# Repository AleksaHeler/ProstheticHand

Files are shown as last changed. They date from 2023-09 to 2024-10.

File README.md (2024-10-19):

# OpenHand
 
Our attempt at a prosthetic hand controlled by muscle EMG sensors, using linear actuators to move mechanically linked fingers. Implementing our own 3D models (ME), schematic & PCB design of main control board (EE) and software solution (SW).

## Proof of concept

Our (actually second) proof of concept, is using our own PCBs with STM32, our own mechanical design, and some basic software running on STM32 reacting on button press or EMG sensor activation.

For now, this approach seems promising, and only thing left to be changed is the motors used. We use linear actuators, which seem to be exactly what we need, but for now they don't have any position feedback. To solve that we will be using motors with built-in encoders in future, and monitoring their position with STM32 HW timer functions for encoders. Preliminary testing for that worked perfectly, we could always know the position of the motor based on the encoder value, and using endstops we can also calibrate the travel, and using current limiting H bridge motor drivers, we can control the force applied. 

Here are some screenshots of the current status:

### Finger design. Completely mechanical linkage, with linear actuator
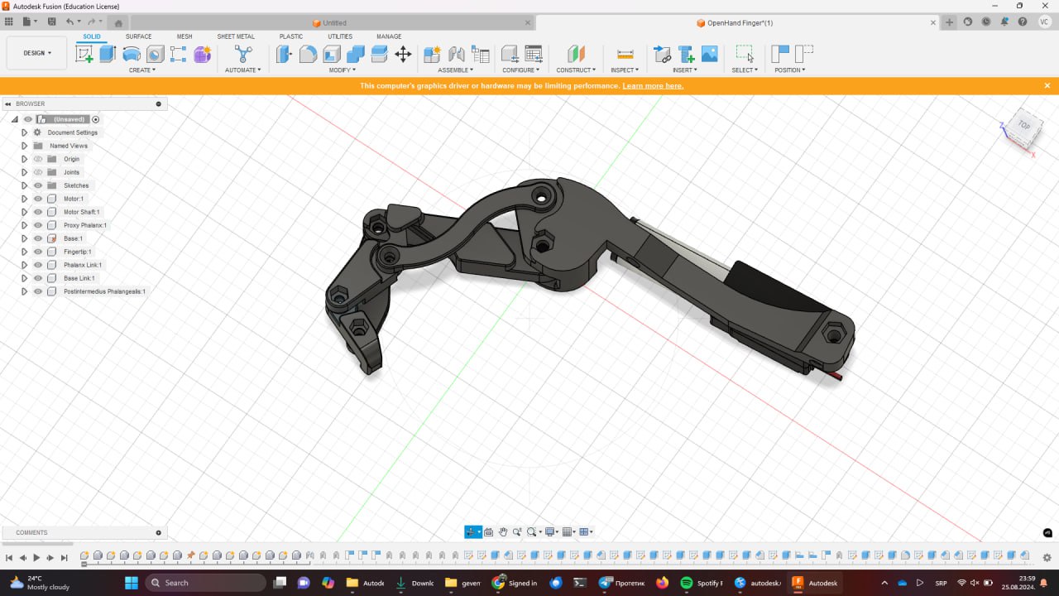
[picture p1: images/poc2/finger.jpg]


### Our custom PCB, with many components including EMG sensors, H bridge motor drivers, etc.
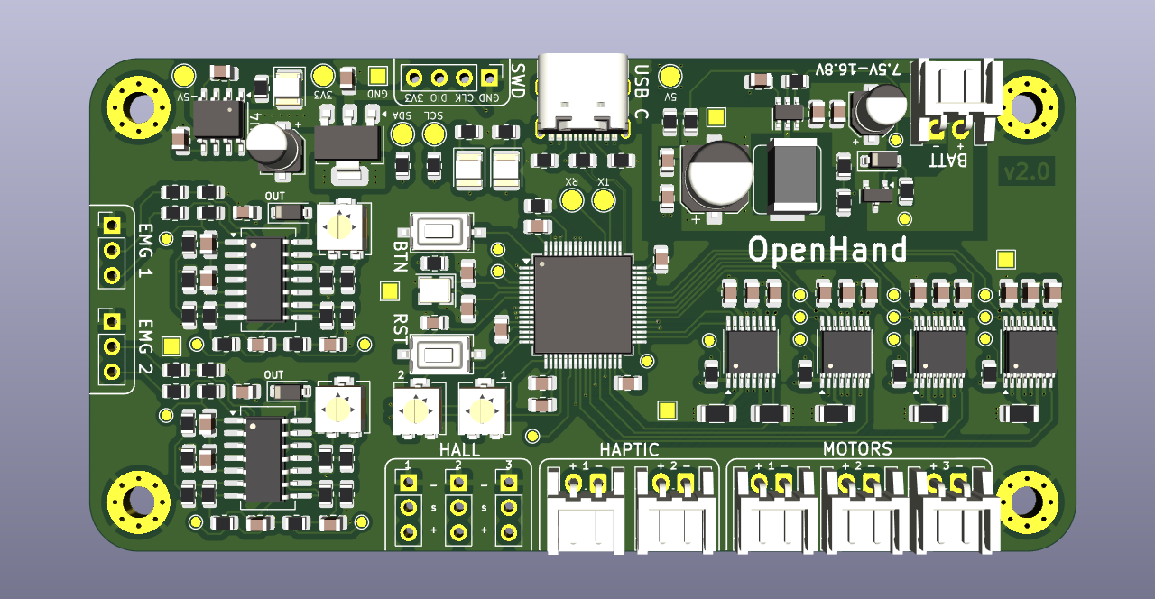
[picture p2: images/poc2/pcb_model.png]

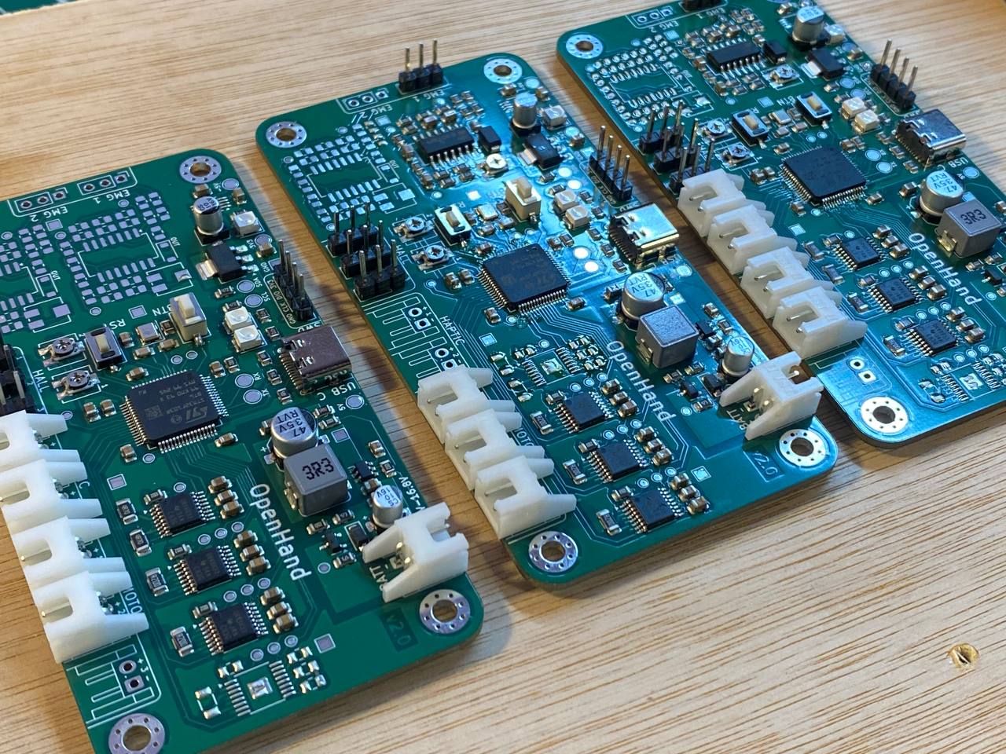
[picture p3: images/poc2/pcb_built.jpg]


### Also some EMG sensor readings (before additional filtering)
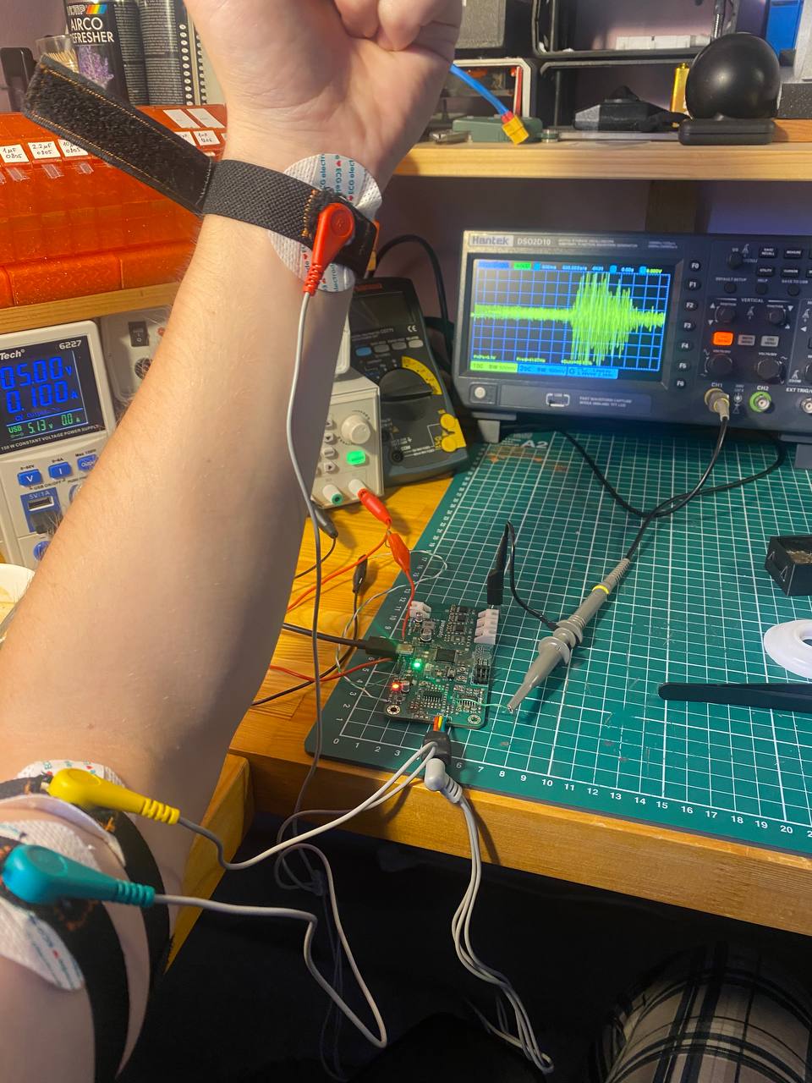
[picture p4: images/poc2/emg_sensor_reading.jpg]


### Now, the whole prototype of the hand (3D printed, batteries, PCB, 3x fingers with motors)
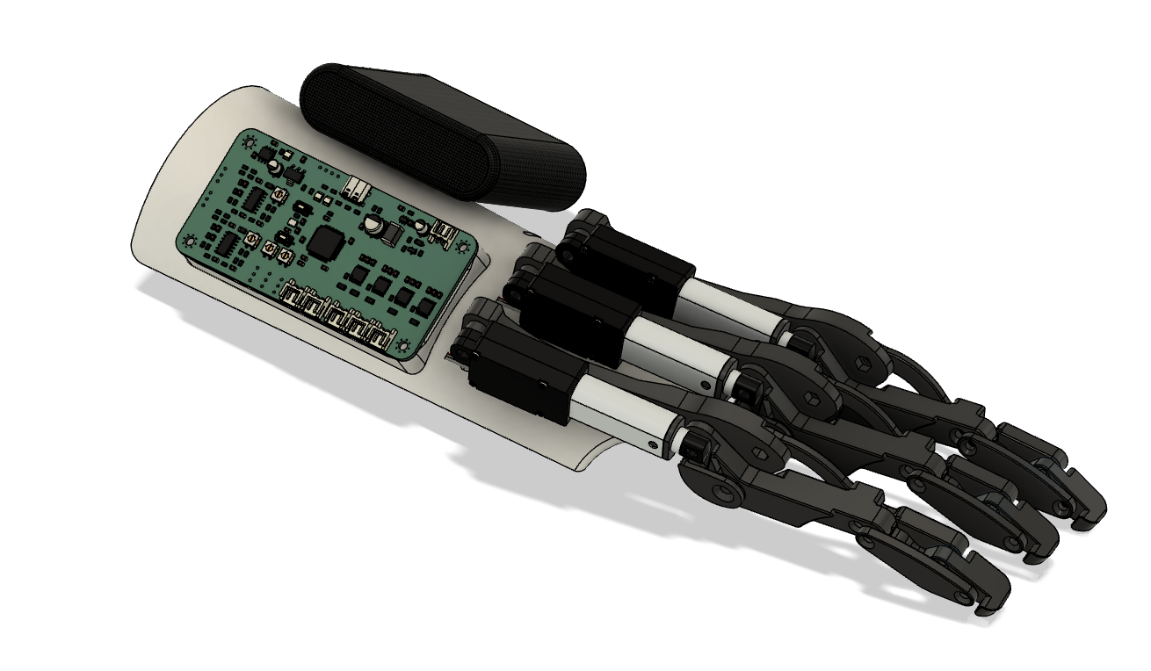
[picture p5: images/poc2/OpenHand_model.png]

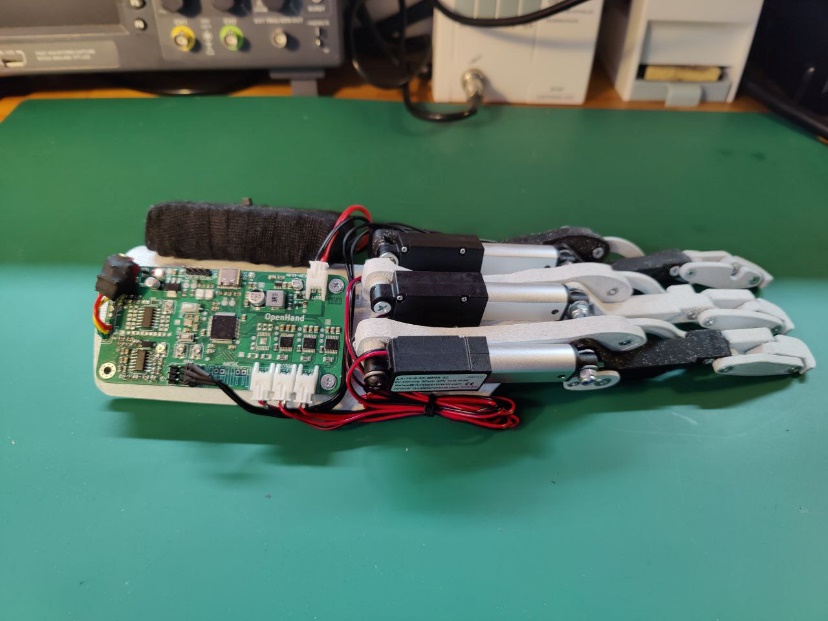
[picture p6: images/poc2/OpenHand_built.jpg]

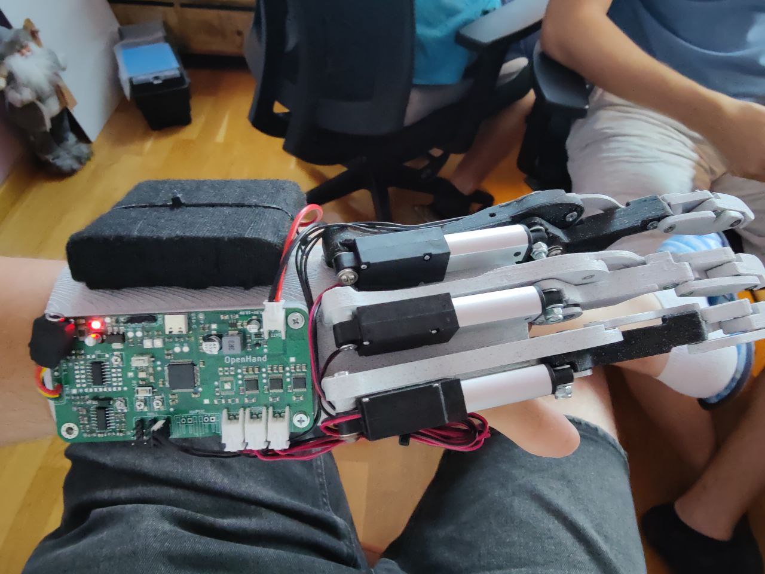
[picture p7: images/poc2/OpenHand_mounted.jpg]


## Example videos of OpenHand in action

Here are some videos of the project for now. Nice to see it finally come together, although this is still early in development, and some things will be changed, and a lot of things will be made to look even prettier.

Note: you might have to download .mp4 videos if GitHub doesn't support playback in browser.

### Showing the response when EMG reading muscle activity 
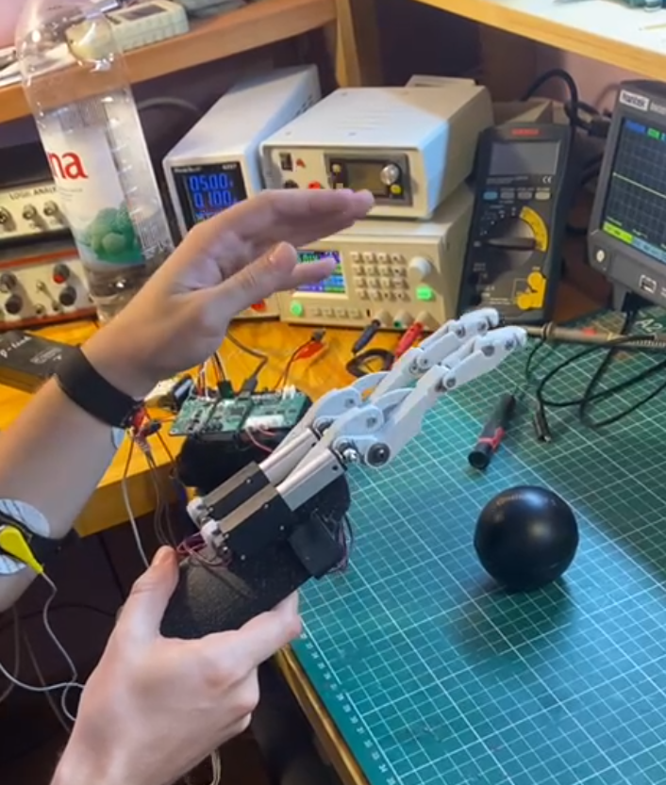
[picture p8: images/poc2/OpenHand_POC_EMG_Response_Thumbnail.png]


### Simple demonstration of holding a bottle
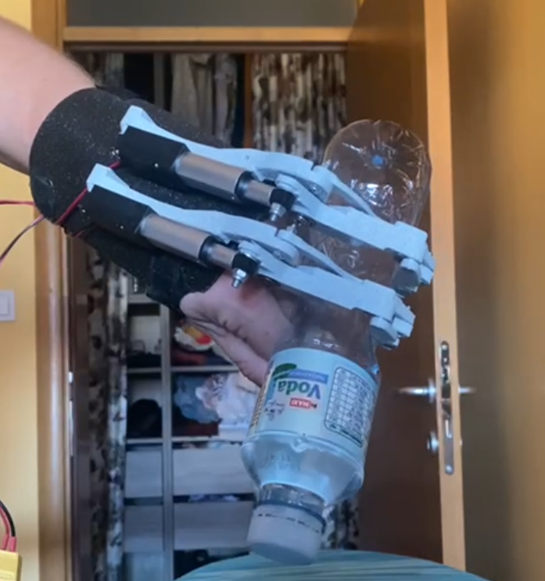
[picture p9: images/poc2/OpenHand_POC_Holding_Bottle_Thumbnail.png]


### Demo: holding a can of soda
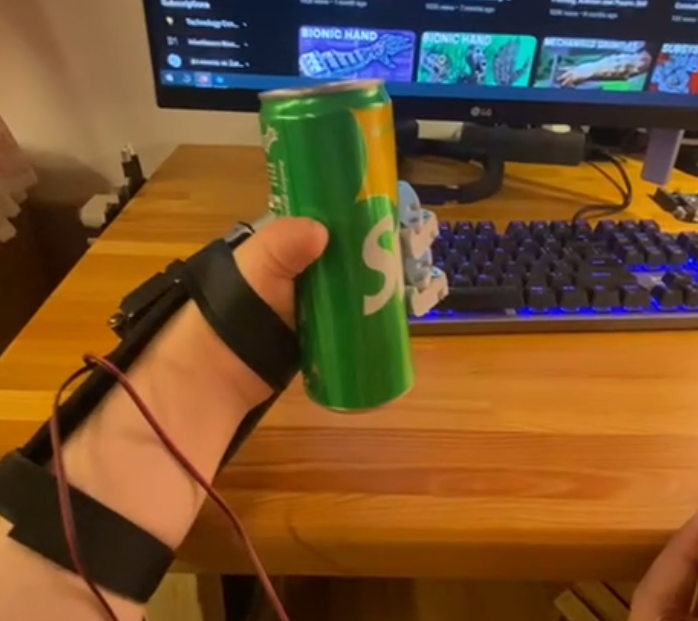
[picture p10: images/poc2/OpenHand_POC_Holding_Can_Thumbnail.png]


### Demo: holding a multimeter
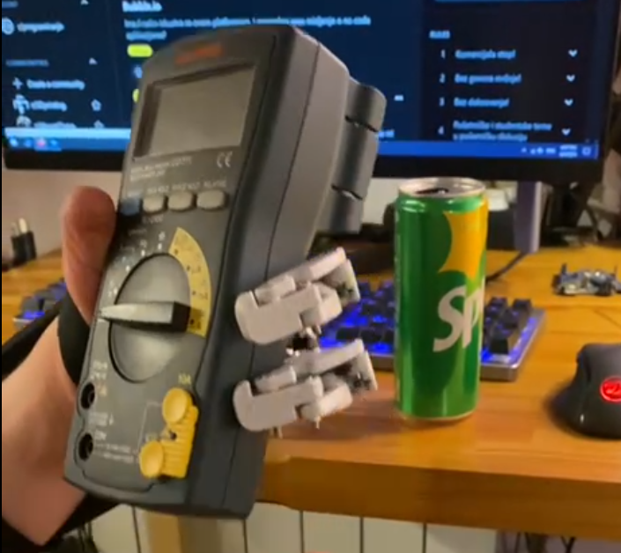
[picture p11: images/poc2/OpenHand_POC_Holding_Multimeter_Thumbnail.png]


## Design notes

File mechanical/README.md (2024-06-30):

# Mechanical designs for the prosthetic hand project

## Initial design based on plaster mold of the hand

In folder **OpenHand** you can find the [Fusion360 file of the prosthetic hand](OpenHand/OpenHand.f3d), described below (as well as a .STEP file).

Here is the (somewhat modified and cleaned up) scan of the plaster/clay mold we made of the base, by pressing it over the arm:
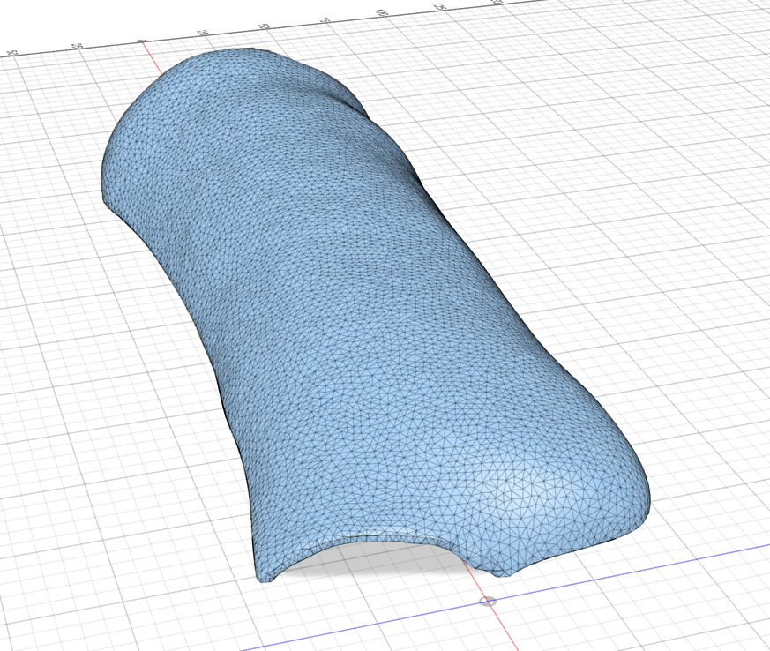
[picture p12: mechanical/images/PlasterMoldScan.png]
Plaster mold


After it is imported into Fusion 360, we can create a more basic shape following its dimensions and profile somewhat, so we will make a parametric design to be later 3D printed:
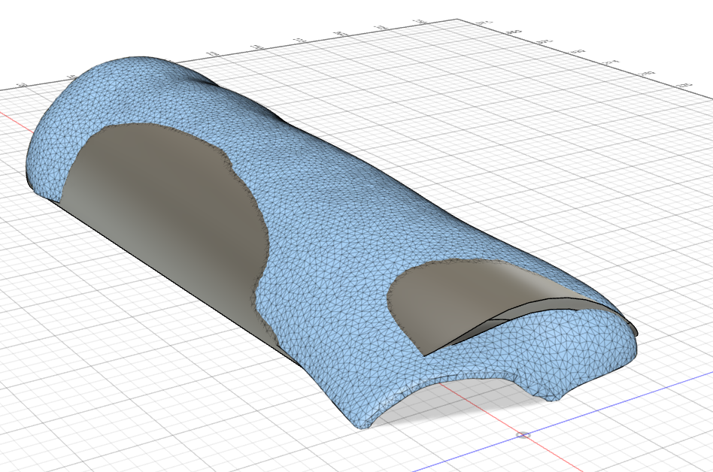
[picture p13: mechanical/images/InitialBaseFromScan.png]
Initial base model


After adding finger design by [fflori4n](https://github.com/fflori4n), motor, PCB and battery 3D models:
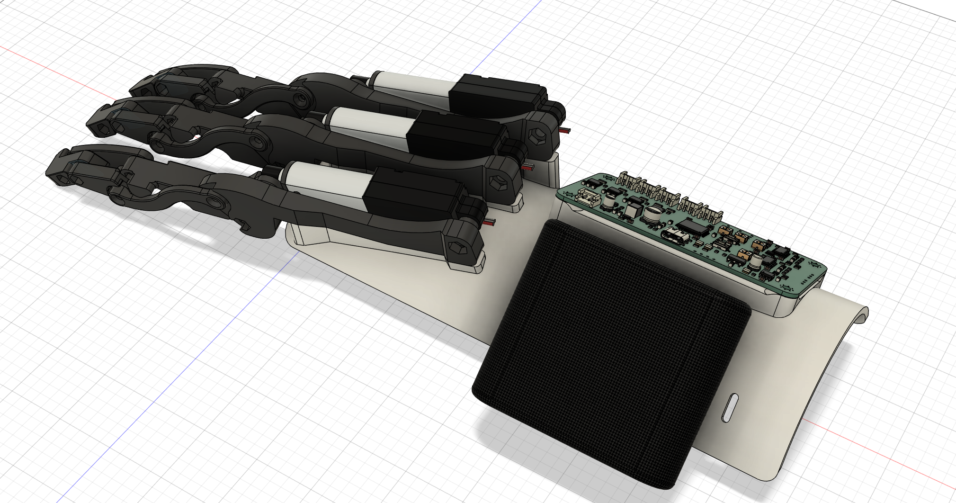
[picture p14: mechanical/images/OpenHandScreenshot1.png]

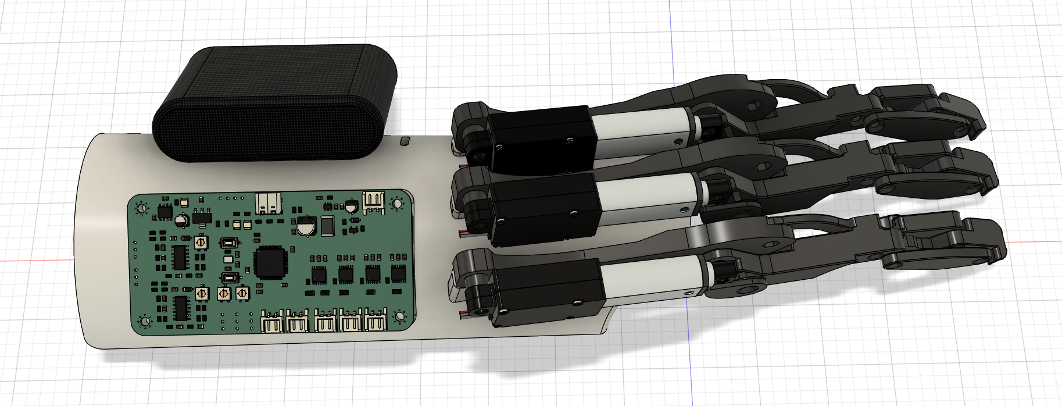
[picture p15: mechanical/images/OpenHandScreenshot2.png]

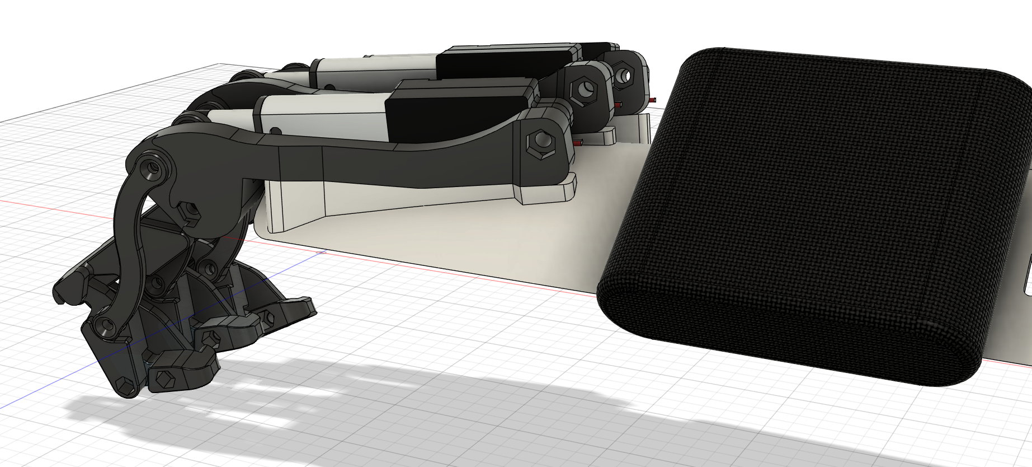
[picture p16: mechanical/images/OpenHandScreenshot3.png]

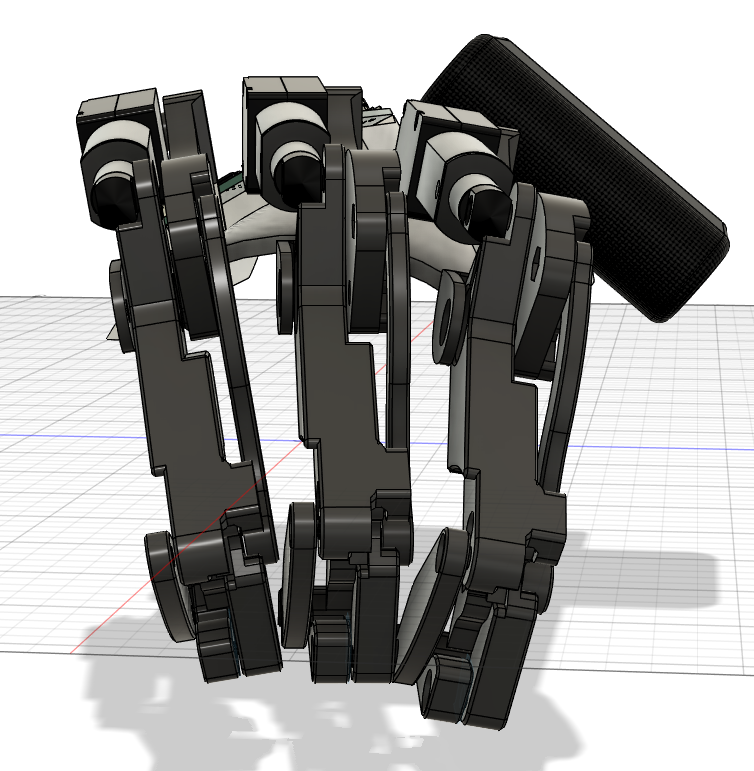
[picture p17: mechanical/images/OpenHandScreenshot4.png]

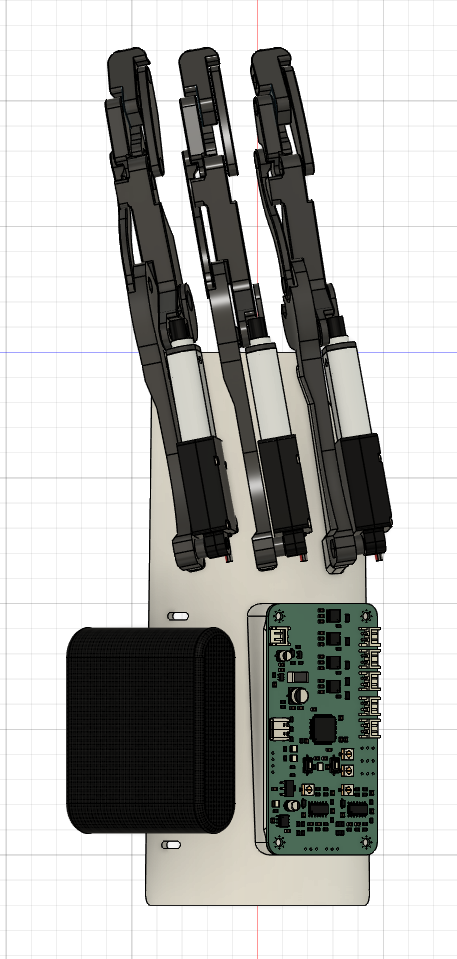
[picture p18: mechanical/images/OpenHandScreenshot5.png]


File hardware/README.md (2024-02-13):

# Hardware & PCB designs of the prosthetic hand project

For designing those we use [KiCAD](https://www.kicad.org/download/). Good tutorial can be found [here](https://www.youtube.com/playlist?list=PL3bNyZYHcRSUhUXUt51W6nKvxx2ORvUQB). Although it's for a bit older version of the KiCAD it is still usefull.

For now we have two designs: DevBoard and OpenHand. First one is for proof of concept, while other one is still in development and meant to be used as initial version to build upon.

## DevBoard

Firstly we haver here a development board, custom made for our purpose of having EMG sensors and servo motors connected. Also a couple of buttons/pots etc. for easier debugging/testing. Schematic can be found [here](DevBoard/schematic.pdf).

We will be using [ESP32 S3](https://api.riot-os.org/group__cpu__esp32__esp32s3.html). So in this desin, we're using the ESP32 S3 devboard, but later on we will just use the ESP32 microprocessor.

The boards will be ordered from an online PCB manufacturer, in our case JLC PCB.

DevBoard features:
 - battery/power supply connector
 - 3x servo connectors (with current sensing over 0.1 ohm shunts, and filter for current sensing signal as it is a bit noisy)
 - 2x EMG sensor connectors (signal goes trough RC low-pass filter on its way to the uC)
 - 4x dip switches for easy configuration (easily change code logic on-the go, without re-flashing the board)
 - 2x push buttons (with on-board pullups and HW debounce filter)
 - 2x trim pots and one 'normal' potentiometer (with RC low-pass filter to get rid of some noise from cheap pots)
 - 2x debug LEDs (red/green)
 - 5V regulator for the ESP32 DevBoard
 - input/battery voltage sensing
 - reverse protection diode (would be nice to upgrade to a 'smarter' variant with MOSFET later)
 - 2 layer PCB, components on one side, mix of SMD/THT components
 - a lot of test point pads on the board for all the signals

For now, this DevBoard should give us enough functionality to make some version of a working prototype, but the wishlist for the actual PCB will be updated as we come across new stuff.

### Devboard pictures

#### Schematic

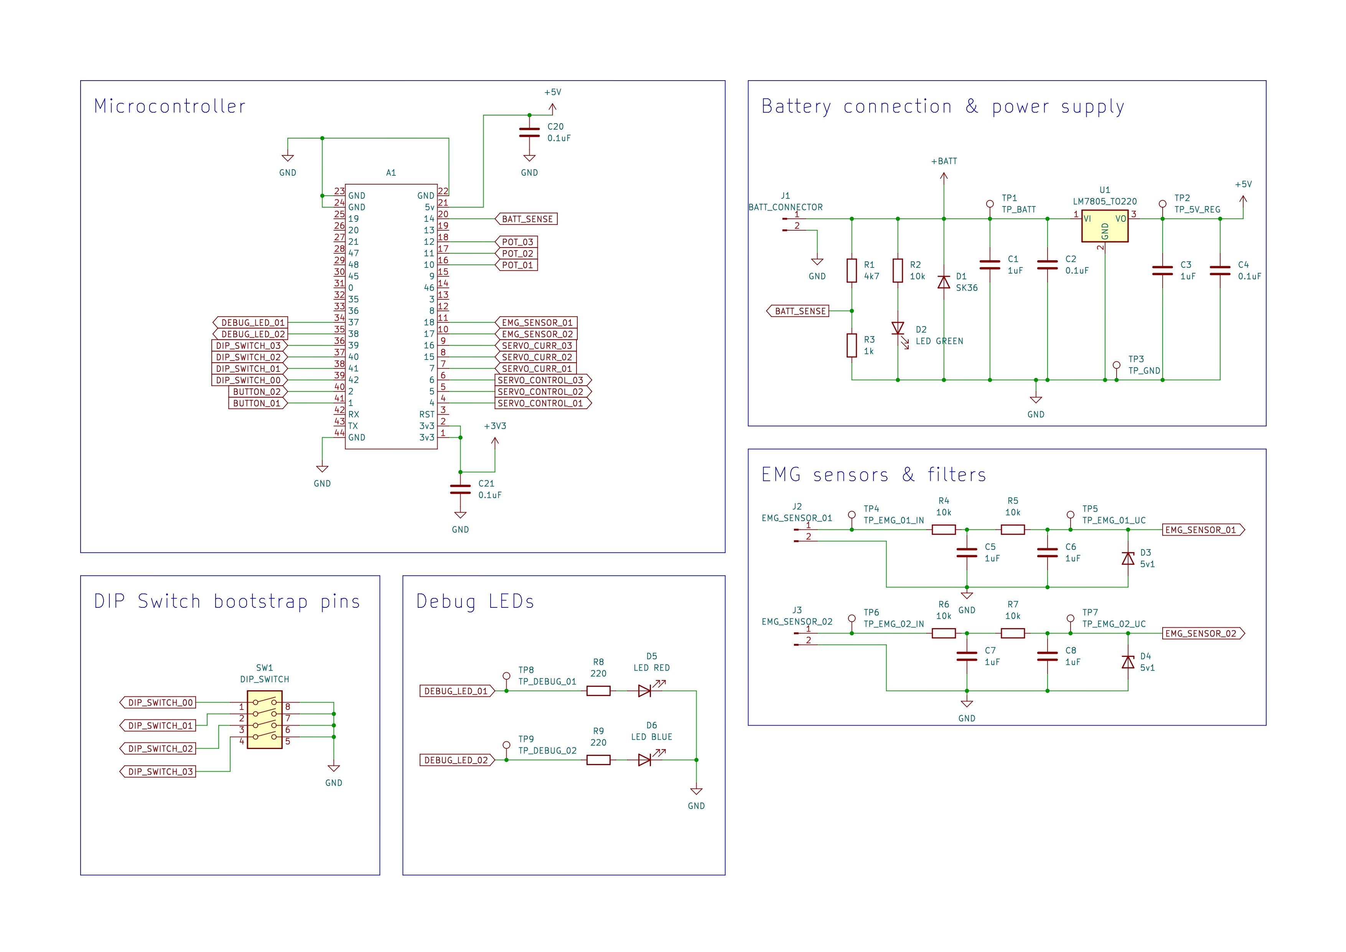
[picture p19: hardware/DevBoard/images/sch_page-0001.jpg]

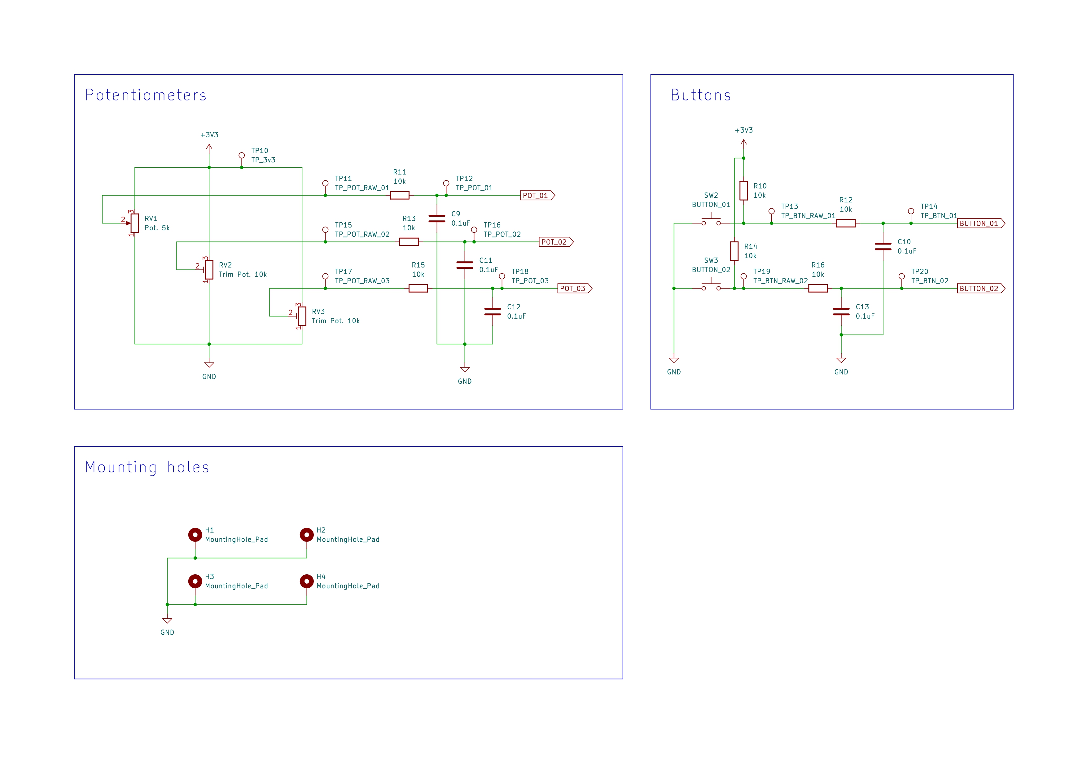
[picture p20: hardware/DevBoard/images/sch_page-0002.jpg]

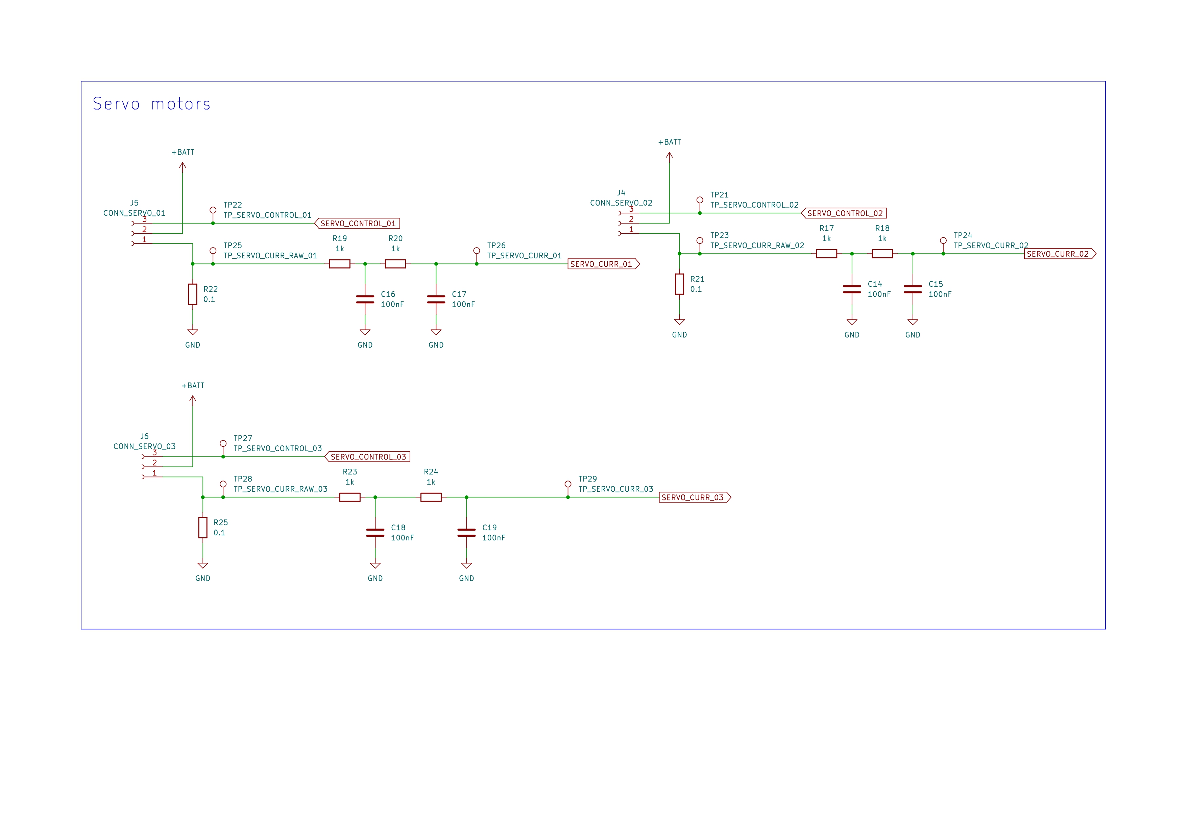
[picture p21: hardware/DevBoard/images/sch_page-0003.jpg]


#### PCB design

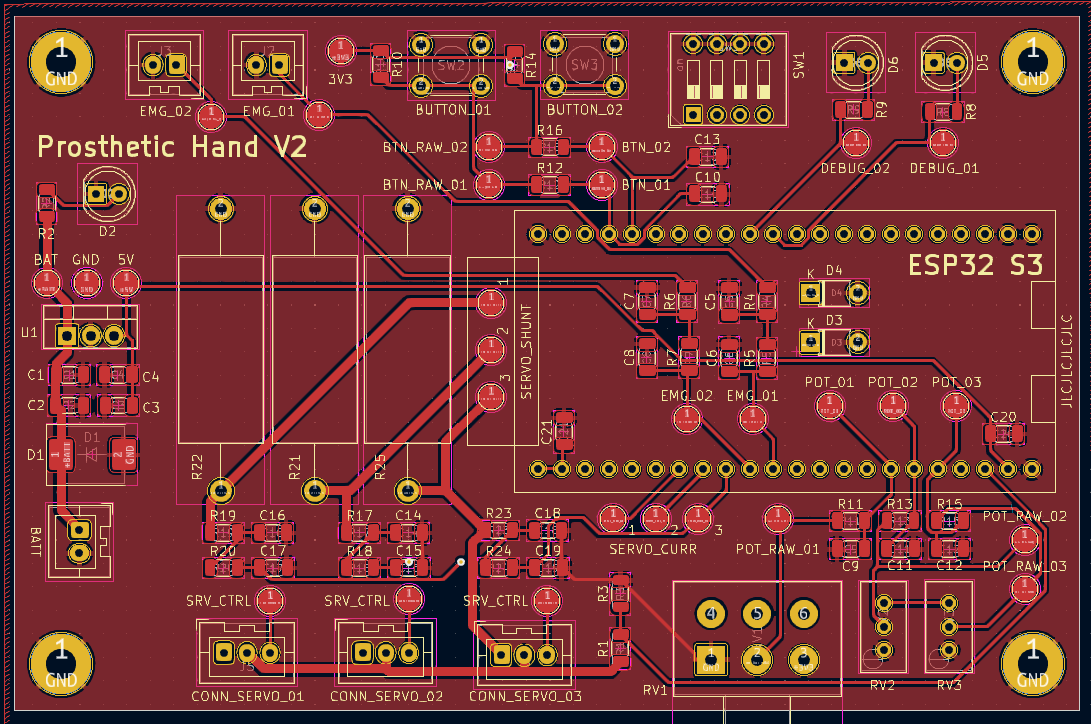
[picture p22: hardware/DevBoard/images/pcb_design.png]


#### Manufactured PCB

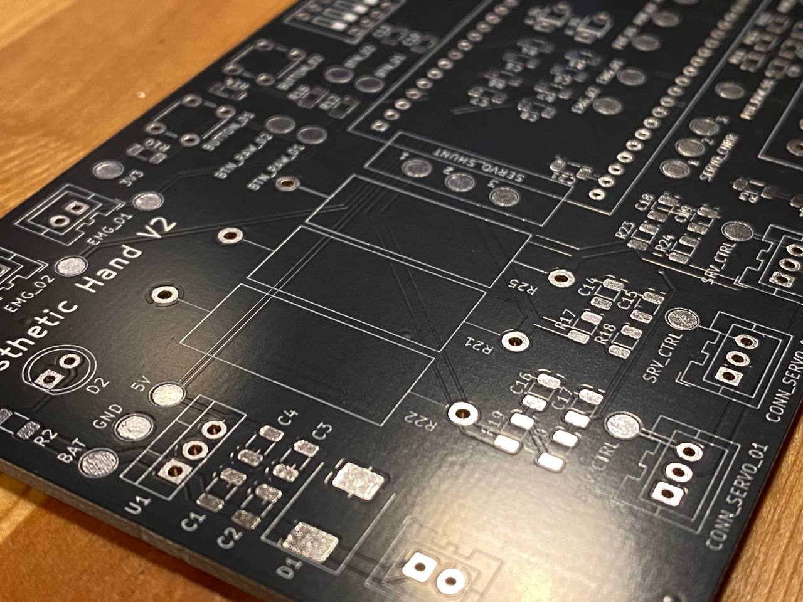
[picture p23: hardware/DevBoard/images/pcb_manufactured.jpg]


#### Assembled PCB

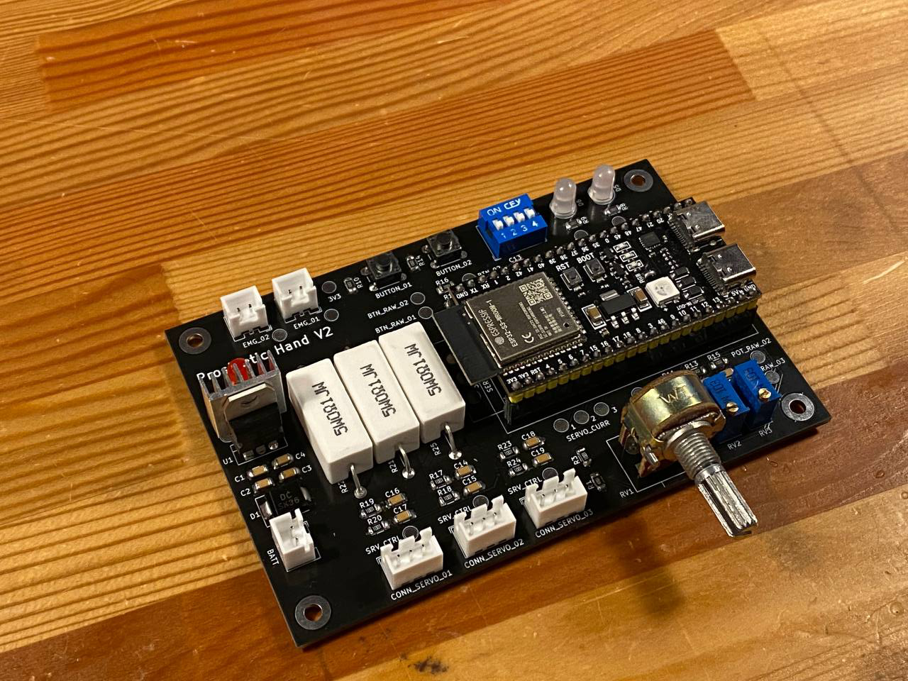
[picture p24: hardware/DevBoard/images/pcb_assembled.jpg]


### Devboard testing

#### Smoke test

When powered from a 12V power supply, the board turns on, power LED is on, nothing caught fire, microcontrollers LED flashing, debug LED flashing (as defined in code). 5V regulator (LM7805) is giving us 5V.

#### Filter testing: EMG sensor

Filter is working. On a screenshot below, channel 1 is raw signal from signal generator which we feed into EMG sensor input, and channel 2 is measured on testpoint for EMG input on the microcontroller. We have a two stage RC low-pass filter with values 10kOhm and 1uF (see shemcatic sheet 1).

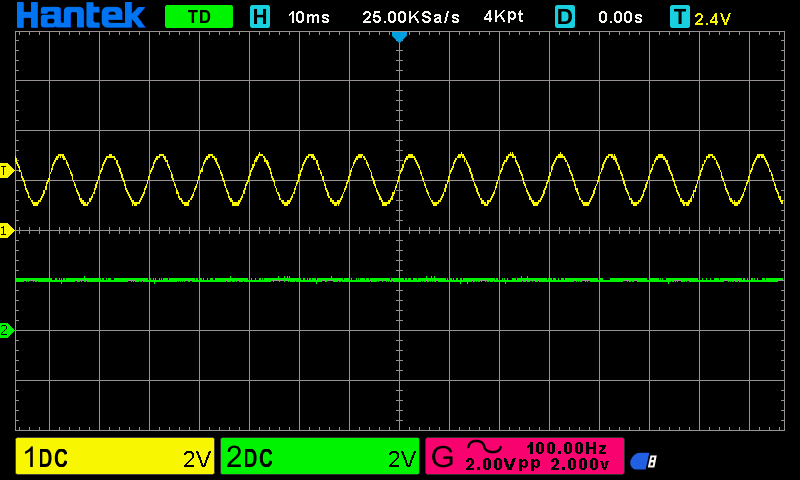
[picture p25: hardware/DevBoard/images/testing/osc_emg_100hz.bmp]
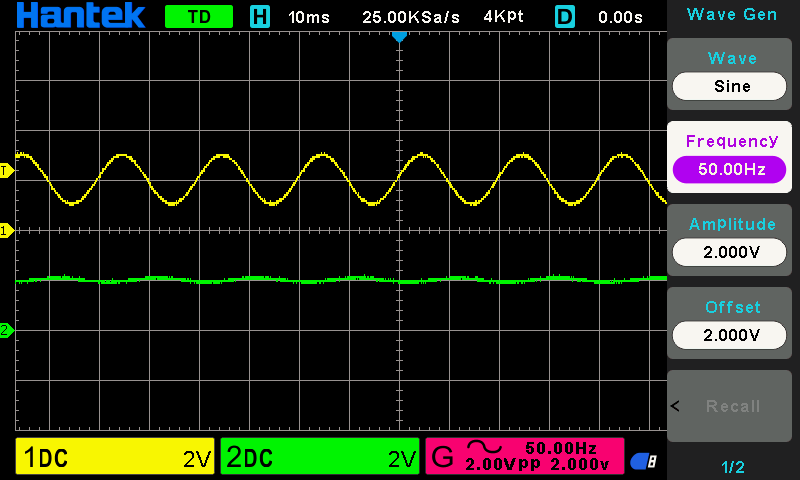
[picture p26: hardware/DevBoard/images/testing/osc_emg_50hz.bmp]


#### Filter testing: Servo current

Servo motor current raw signal is looking quite awful:

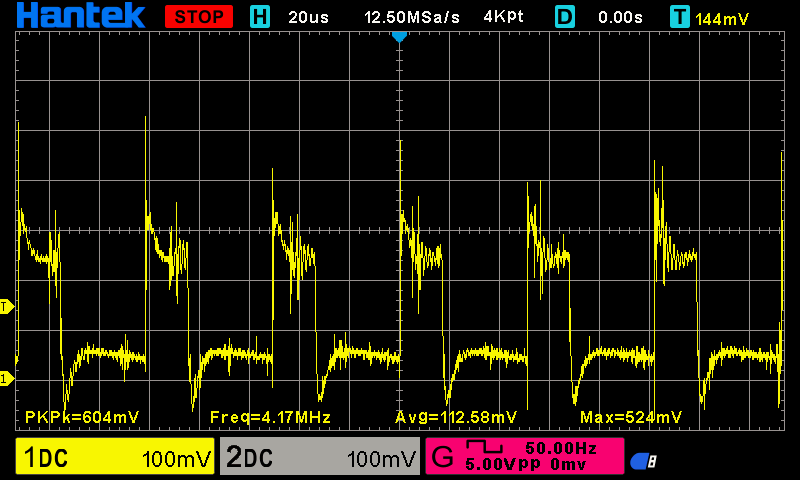
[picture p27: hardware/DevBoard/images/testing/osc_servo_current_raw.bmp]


Here is an example where I connected an external supply to push 1A trough the shunt resistor. Chn 1 is raw, chn 2 is filtered. We can see its filtering enough for now.

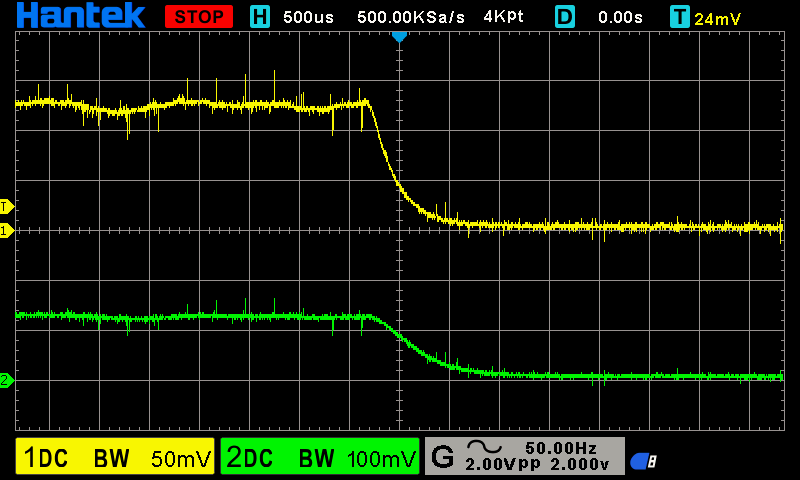
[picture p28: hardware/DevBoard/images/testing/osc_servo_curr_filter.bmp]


#### Filter testing: Button debounce

Similar to EMG sensor, here we see channel 1 is raw button signal, and channel 2 is filtered. We can see the filter is doing its job on and filtering the contact bouncing:

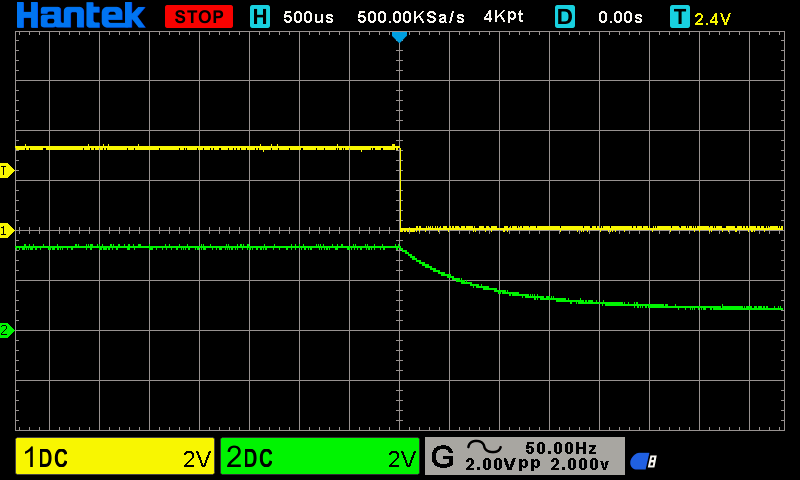
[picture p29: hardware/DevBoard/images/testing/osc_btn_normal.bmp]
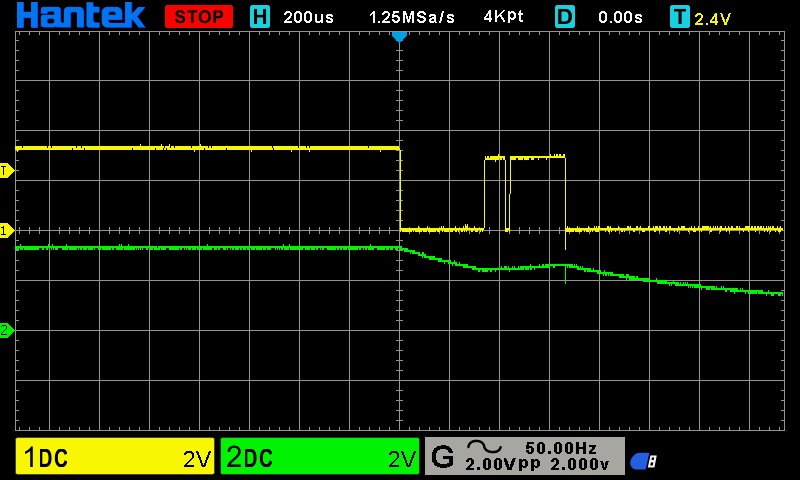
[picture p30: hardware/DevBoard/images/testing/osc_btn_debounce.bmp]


#### Filter testing: Pot debounce

I could not get the pot to give us errors (jumping to gnd of supplied voltage), so it seems the pot is good after all. Although during previous testing some pots were getting some pretty wild oscillations just by tapping them.

#### Input voltage divider

With 10V on input from a bench power supply, at battery sense voltage divider we get 9.97V as input, and output at 1.753V measured with multimeter - as expected (from calculation: 1.754V with 4k7 and 1k resistors in divider).

## OpenHand PCB

Work in progress. 

Features:
 - Microcontroller: STM32 or ESP32, still to be decided, will make a version with both of them
 - USB C connector, CH340C USB to UART IC, JTAG for debugging
 - On-board 3 cell battery charger (BMS to be implemented on the battery pack)
 - Switch mode power suplly, to generate 5V high current for motors, and 3.3V lower current for microcontroller and sensors
 - On-board EMG sensor processing (from raw electrode connections)
 - Some user interaction components - trim-pots, debug LEDs, buttons
 - Separate ADC converter over I2C, for battery voltage sensing and hall effect sensors
 - Hall effect sensors for detecting finger position
 - Input reverse polarity protection with MOSFETs
 - Connectors and drivers (separate motor driver IC) for linear actuators instead of servo motors (H-bridge)
 - Connectors and drivers for haptic feedback (vibrating motor, similar to a console joystick vibration)

Schematic and project can be found [here in OpenHand folder](OpenHand/OpenHand.kicad_pro).

Schematics for now:

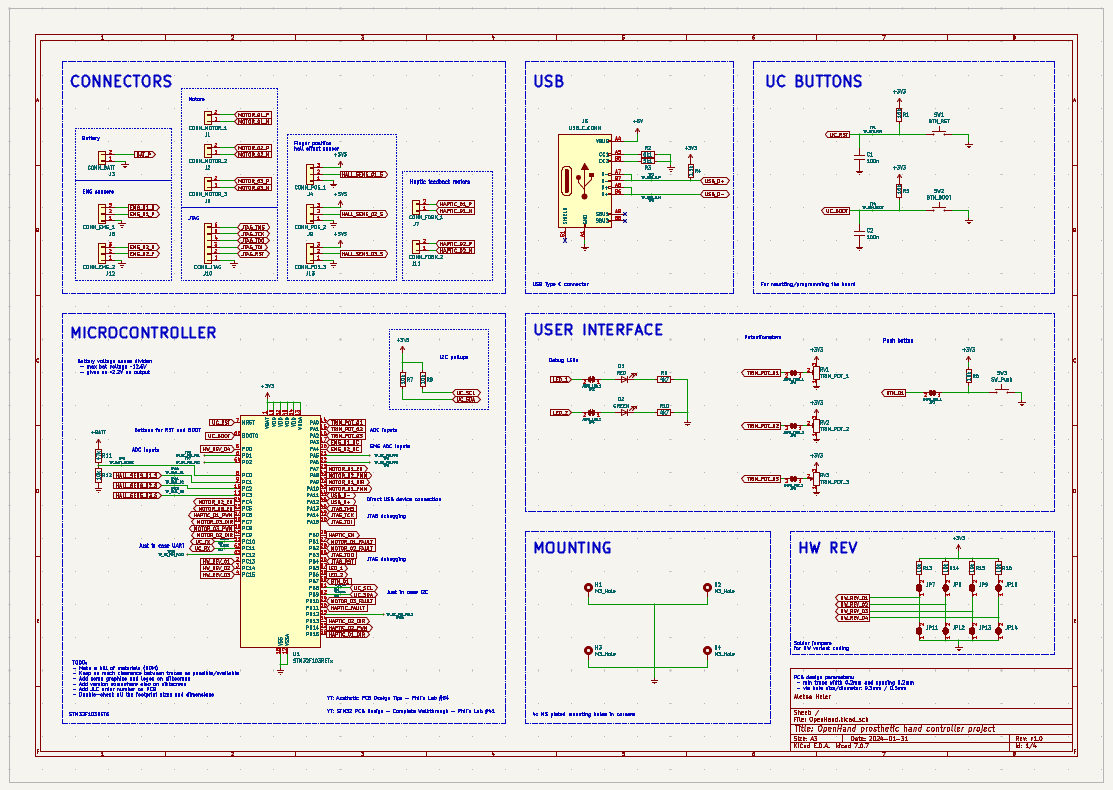
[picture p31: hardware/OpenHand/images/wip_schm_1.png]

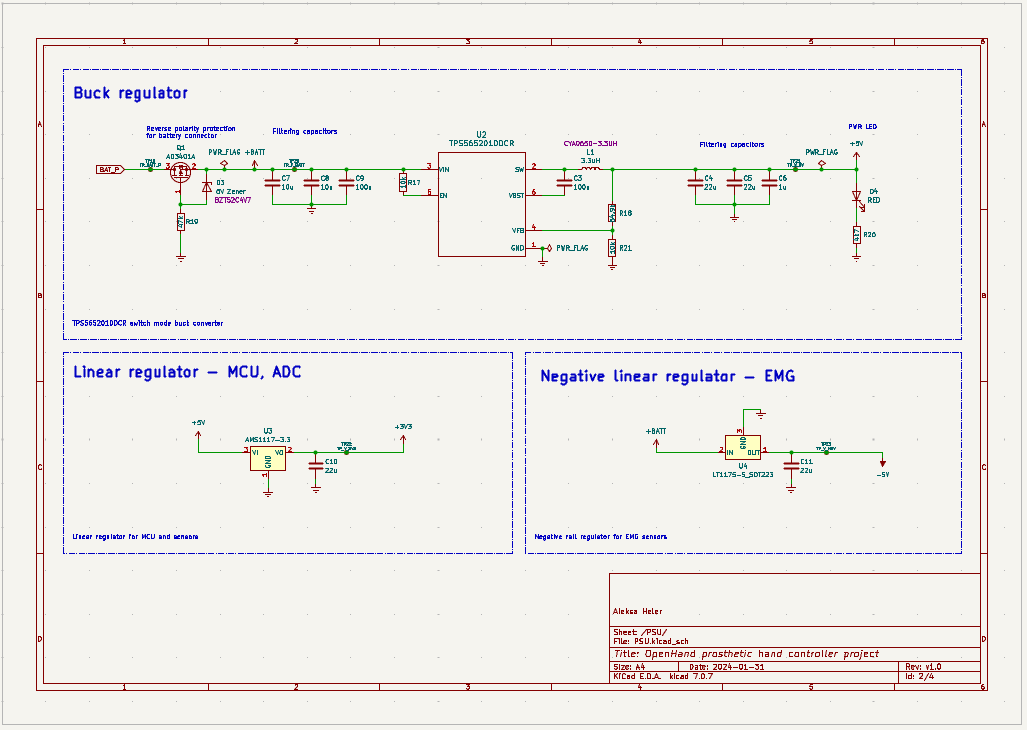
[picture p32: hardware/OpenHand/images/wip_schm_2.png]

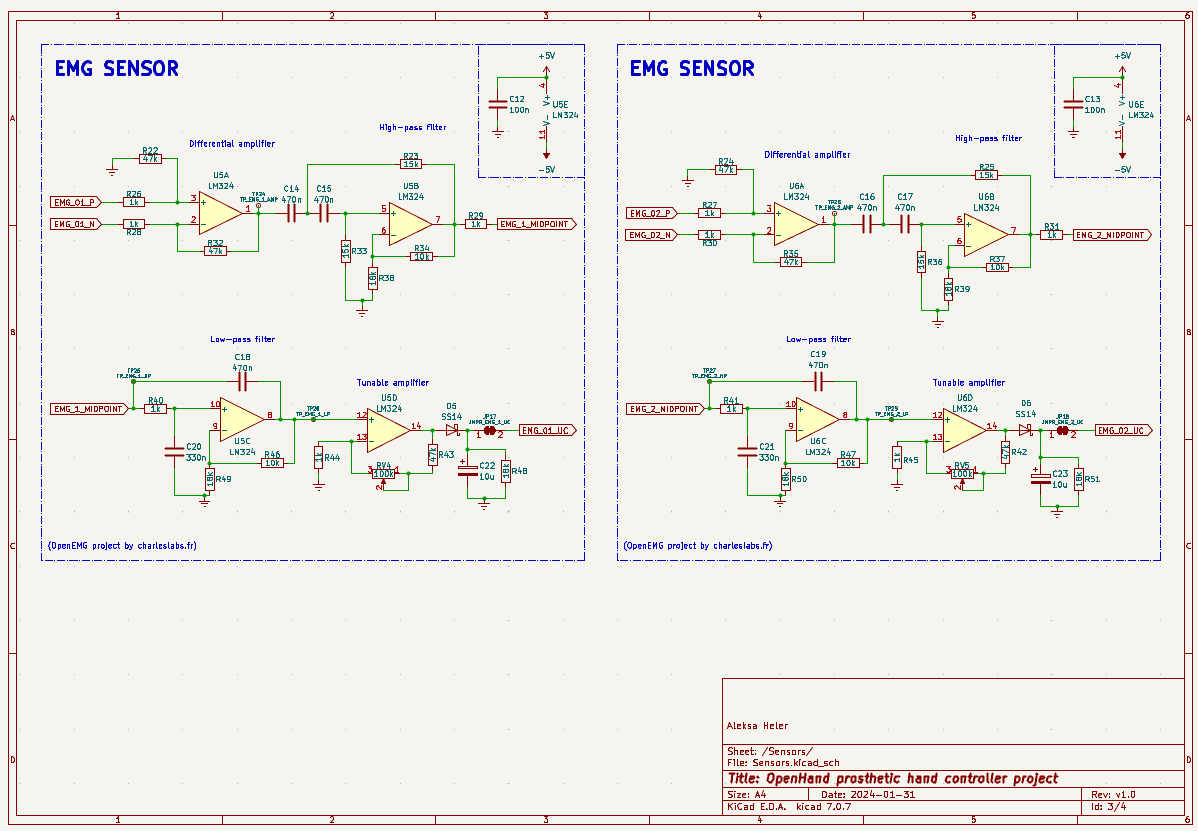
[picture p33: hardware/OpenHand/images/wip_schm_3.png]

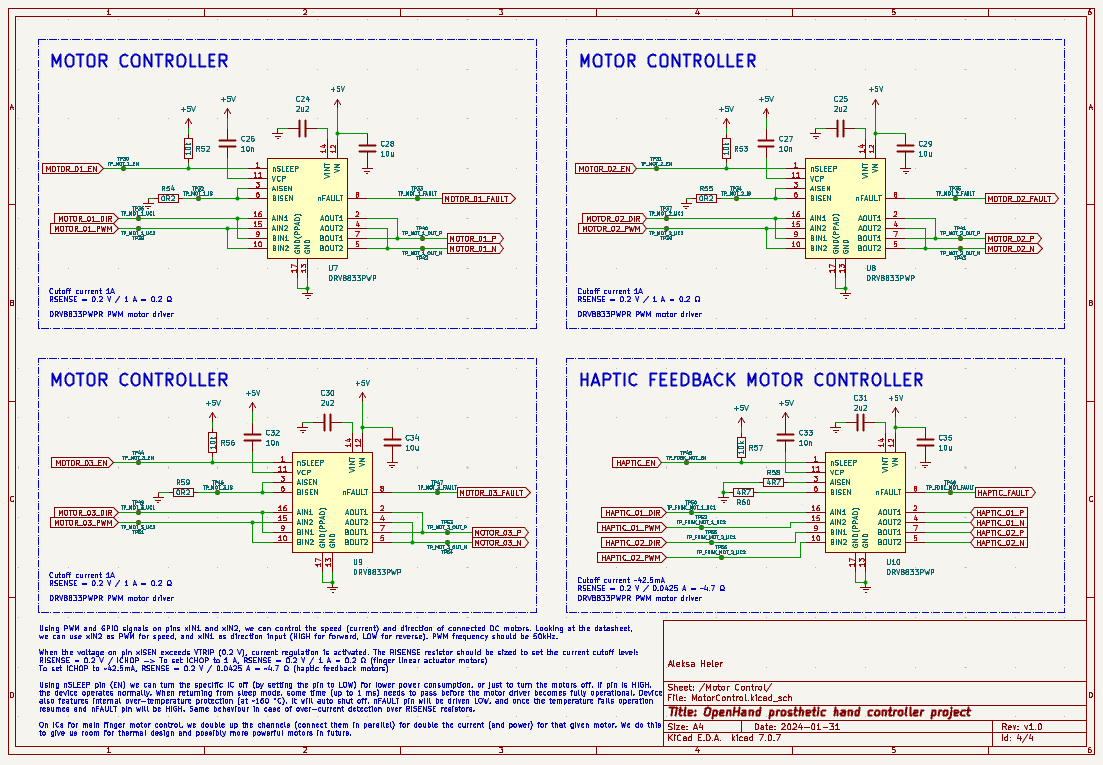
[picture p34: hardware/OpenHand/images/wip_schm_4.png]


Layou for now:

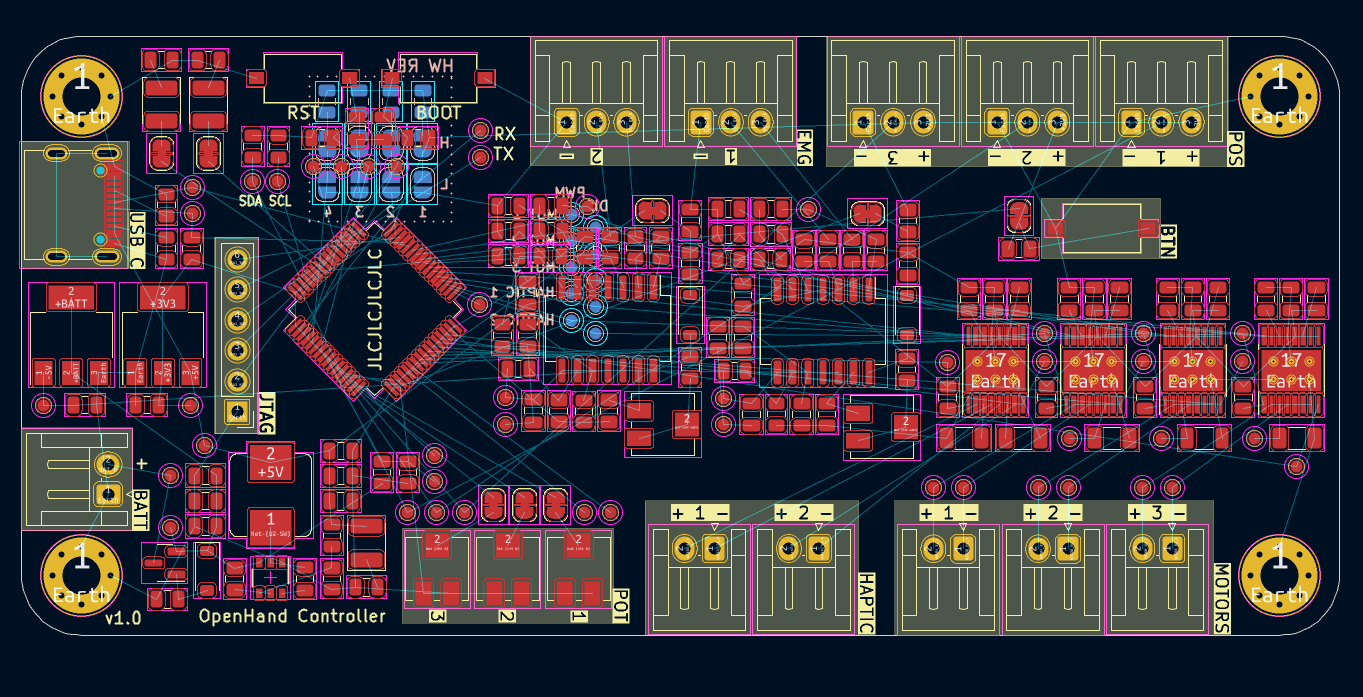
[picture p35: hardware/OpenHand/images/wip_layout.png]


3D PCB view for now:



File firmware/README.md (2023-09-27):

# Firmware/software for the Prosthetic Hand project

Within this directory, you can find the **ProstheticHand** [PlatformIO](https://platformio.org/) project created in the [Visual Studio Code](https://code.visualstudio.com/download) editor.  
The [SEGGER J-Link debug probe](https://www.segger.com/products/debug-probes/j-link/) is used for code flashing and debugging.  
Below is the step by step process on how to set the project up and compile it for the first time:
 - __Install [Visual Studio Code](https://code.visualstudio.com/download)__
 - __Install the [PlatformIO](https://platformio.org/install/ide?install=vscode) plugin__ for Visual Studio Code
 - __Install the [J-Link Software](https://www.segger.com/downloads/jlink/)__ from SEGGER (Choose the installer based on your operating system, leave all settings at their default values during installation)
 - __Clone the project's git repository__
 - __Open the _ProstheticHand_ project__ from PlatformIO's home screen
 - When opening the project for the first time, PlatformIO should automatically update and download necessary dependencies and configure the project.
 - Try to __build the code__. It should work without issues.
 - If there are issues, __ensure that the correct USB driver is installed__, as it is required for the J-Link debugger to function.
  For Windows, we used the WinUSB driver. If it's missing, you can use [Zadig](https://zadig.akeo.ie/) to install it. (Our example driver version is v6.1.7600.16385.)
 - With the J-Link connected and the ESP32 powered on, you should be able to upload the code using the J-Link debugger, as well as debug it.

If you want to use the serial monitor with the ESP32, you may need to install drivers for its onboard USB to UART bridge:
 - __Identify the USB to UART bridge__ on your ESP32 board
 - __Find and install the driver__
 You can find most USB to UART bridge chips included on ESP32 development boards listed [here](http://esp32.net/usb-uart/), together with the necessary drivers
 
 Note: You can install the [Serial Monitor](https://marketplace.visualstudio.com/items?itemName=ms-vscode.vscode-serial-monitor) extension for Visual Studio Code, which provides a more organised interface compared to PlatformIO's built-in serial monitor.

## Code guide / developer guide

All the source code files are in **src** folder. In there you can find a couple of folders/files:
 - main.cpp - entry point of the application
 - config - contains header files for defines and typedefs, version information and includes used in the whole project 
 - include - contains 'libraries' used in project. In quotations since they are not exatcly libraries but can be considered as such let's say
 - drivers - contains the actual components of the program, functional codes that behave as components/objects (each has init and handle function and implements its own logic)

All .cpp files (for example **main.cpp**) shall have a **main_e.h** (external) and **main_i.h** (internal). Using this approach we can have private and public global variables and functions, which can be useful in such a project. For example we can have 'init' and 'handle' functions declared in external header file and helper functions used for internal logic defined in internal header. Next, the main module (or anywhere this code is used) can include only the _e.h file, and thus only have access to what is needed to use the module, and not the internal logic stuff.

**Naming convention** used: *main_f_Handle_v*, *btn_BtnStates_u8*, *pot_g_PotConfig_s*
 - first is the module name (main, btn, pot, srv...)
 - then kind of literal (f - function, g - global var, s - struct, c - constant...)
 - then the name (in upper camel case - UpperCamelCase)
 - finally the type, or return type for function (v - void, p - pointer, u32 - unsigned 32bit int, f64 - 64bit float...)

We have main.cpp as entry point, and then it manages all the other drivers (logical components: buttons driver, potentiometer driver, servo driver...). This means that in the main program, we have two functions: **main_f_Init_v** and **main_f_Handle_v**. In the init function, the main calls each drivers init function (*btn_Init_v*, *pot_f_Init_v*) once during boot, and then goes on to call the handle function in loop while the device is running (*btn_Handle_v*, *pot_f_Handle_v*). Each module handles internal logic on its own, and some modules, for example servo driver, take other modules outputs (like button and pot states) and use them, like in the servo driver it uses pot to set the angle of the servo. This is used in order to be more modular and to have easier time implementing smaller software components instead of spaghetti code.

**Main code** has init and handle functions, and is primarily focused on calling each modules init and handle function. But it does that in a way that we have a **10ms repeating loop**, where during each 1ms subdivision we handle some of the functionality. So for example during first 1ms it will call one drivers handle function, then in the next 1ms it will call another and so on, until we loop back after 10ms total. This is done in order to better distribute load over time, and to provide us with easier way of measuring runtime durations and to find parts of code that take too much time, and in that case, perhaps distribute it over couple of 1ms tasks.

## Using the program

If serial degbug is enabled, the output to console for now looks like this:
```
----------------------------------------
 > runtimes (in microseconds):
    ├─[0] curr: 14, min: 13, max: 73
    ├─[1] curr: 715, min: 702, max: 843
    ├─[2] curr: 24, min: 23, max: 81
    ├─[3] curr: 1, min: 1, max: 1
    ├─[4] curr: 1, min: 1, max: 1
    ├─[5] curr: 1, min: 1, max: 1
    ├─[6] curr: 1, min: 1, max: 1
    ├─[7] curr: 1, min: 1, max: 1
    ├─[8] curr: 1, min: 1, max: 1
    ├─[9] curr: 1, min: 1, max: 1
btns:  0  0  0  0
pots:  179.96  30.22  0.00
servo working
```
Here we can see the above-mentioned 10 x 1ms tasks with each tasks current execution time, min and max times. Also each driver can implement its own serial debug function where it displays useful data to serial (button states, pot values, if servo driver is running...)
Hopefully we will soon update this to use json format, as it will then be easier to use with some other program on the PC for visualising the data.

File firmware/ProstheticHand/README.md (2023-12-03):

# Firmware/software for the Prosthetic Hand project

Within this directory, you can find the **ProstheticHand** [PlatformIO](https://platformio.org/) project created in the [Visual Studio Code](https://code.visualstudio.com/download) editor.
Before we used the [SEGGER J-Link debug probe](https://www.segger.com/products/debug-probes/j-link/) for code flashing and debugging, but currently we use ESP32 S3 built in flash driver. 

Below is the step by step process on how to set the project up and compile it for the first time:
 - __Install [Visual Studio Code](https://code.visualstudio.com/download)__
 - __Install [ESP IDF](https://docs.espressif.com/projects/esp-idf/en/latest/esp32/get-started/windows-setup.html)__ (make sure to download ESP-IDF vX.X.X - Offline Installer)
 - __Install the [PlatformIO](https://platformio.org/install/ide?install=vscode) plugin__ for Visual Studio Code
 - __[Optional] Install the [J-Link Software](https://www.segger.com/downloads/jlink/)__ from SEGGER (Choose the installer based on your operating system, leave all settings at their default values during installation)
 - __Clone the project's git repository__
 - __Open the _ProstheticHand_ project__ from PlatformIO's home screen
 - When opening the project for the first time, PlatformIO should automatically update and download necessary dependencies and configure the project. That might take a couple of minutes
 - Try to __build the code__. It should work without issues
 - If there are issues, __ensure that the correct USB driver is installed__, as it is required for the J-Link debugger to function.
  For Windows, we used the WinUSB driver. If it's missing, you can use [Zadig](https://zadig.akeo.ie/) to install it. (Our example driver version is v6.1.7600.16385.). ESP32 S3 uses __CP210x__ driver.
 - With the ESP32 powered on and plugged in, you should be able to upload the code

If you want to use the serial monitor with the ESP32, you may need to install drivers for its onboard USB to UART bridge:
 - __Identify the USB to UART bridge__ on your ESP32 board
 - __Find and install the driver__
 You can find most USB to UART bridge chips included on ESP32 development boards listed [here](http://esp32.net/usb-uart/), together with the necessary drivers
 
**Note for serial monitor**: You can install the [Serial Monitor](https://marketplace.visualstudio.com/items?itemName=ms-vscode.vscode-serial-monitor) extension for Visual Studio Code, which provides a more organised interface compared to PlatformIO's built-in serial monitor.

**Note for debug**: For debugging with ESPs internal JTAG over USB, first make sure you installed [ESP IDF from here](https://docs.espressif.com/projects/esp-idf/en/latest/esp32/get-started/windows-setup.html) (make sure to download ESP-IDF vX.X.X - Offline Installer), then use Zadig to install "__USB Serial (CDC)__" driver on "__USB JTAG/Serial debug unit (Interface 0)__" [(useful article for this)](https://community.platformio.org/t/how-to-use-jtag-built-in-debugger-of-the-esp32-s3-in-platformio/36042), and "__libusb-win32 (v1.2.7.3)__" driver on "__USB JTAG/Serial debug unit (Interface 2)__" (when you install this driver, the displayed name in driver field will be "usbser (v1.0.0.0)").

## Code guide / developer guide

All the source code files are in **src** folder. In there you can find a couple of folders/files:
 - main.cpp - entry point of the application
 - config - contains header files for defines and typedefs, version information and includes used in the whole project 
 - include - contains 'libraries' used in project. In quotations since they are not exatcly libraries but can be considered as such let's say
 - drivers - contains the actual components of the program, functional codes that behave as components/objects (each has init and handle function and implements its own logic)

Code is broken up into different drivers/modules. Each module is usually responsible for group of input or output type. For example there is a driver for button inputs, for servo output, sensor input etc.

All .cpp files (for example **main.cpp**) shall have a **main_e.h** (external) and **main_i.h** (internal). Using this approach we can have private and public global variables and functions, which can be useful in such a project. For example we can have 'init' and 'handle' functions declared in external header file and helper functions used for internal logic defined in internal header. Next, the main module (or anywhere this code is used) can include only the _e.h file, and thus only have access to what is needed to use the module, and not the internal logic stuff.

**Naming convention** used: *main_f_Handle_v*, *btn_BtnStates_u8*, *pot_g_PotConfig_s*
 - first is the module name (main, btn, pot, srv...)
 - then kind of literal (f - function, g - global var, s - struct, c - constant...)
 - then the name (in upper camel case - UpperCamelCase)
 - finally the type, or return type for function (v - void, p - pointer, u32 - unsigned 32bit int, f64 - 64bit float...)

We have main.cpp as entry point, and then it manages all the other drivers (logical components: buttons driver, potentiometer driver, servo driver...). This means that in the main program, we have two functions: **main_f_Init_v** and **main_f_Handle_v**. In the init function, the main calls each drivers init function (*btn_Init_v*, *pot_f_Init_v*) once during boot, and then goes on to call the handle function in loop while the device is running (*btn_Handle_v*, *pot_f_Handle_v*). Each module handles internal logic on its own, and some modules, for example servo driver, take other modules outputs (like button and pot states) and use them, like in the servo driver it uses pot to set the angle of the servo. This is used in order to be more modular and to have easier time implementing smaller software components instead of spaghetti code.

## Implemented modules

### Main module - OS

**Main code** has init and handle functions, and is primarily focused on calling each modules init and handle function. But it does that in a way that we have a **10ms repeating loop**, where during each 1ms subdivision we handle some of the functionality. So for example during first 1ms it will call one drivers handle function, then in the next 1ms it will call another and so on, until we loop back after 10ms total. This is done in order to better distribute load over time, and to provide us with easier way of measuring runtime durations and to find parts of code that take too much time, and in that case, perhaps distribute it over couple of 1ms tasks.

### Battery voltage input (BAT)

Reads analog input voltage on a pin, which is connected to battery input terminal over a voltage divder. It then provides a varialbe __bat_g_BatVoltage_f32__ with exact voltage of the connected battery (where it will write 0V if no battery is connected).

### Button input (BTN)

Reads battery digital inputs, which have internal pullup and the button press pulls these pins low. So it provides an array btn_g_BtnStates_u8 with length equal to number of buttons (2 in our case for now) where it will put value '1' if the button is pressed.

### DIP switch boostrapping pin inputs (DSW)

Code only executed once during startup. It reads a couple (4 for now) Dual In-line Package (DIP) switches similarly to buttons, and based on the switch configuration (0 or 1) it puts them all as bits into dsw_g_HardwareRevision_e, where we can define HW revisions/configurations and what they will do. Will be used for selecting what signals to use to control the servo motors (sensors or pots or something else). This is then used by other modules to know what to do.

### Potentiometer inputs (POT)

Same as buttons, but with analog inputs. It puts values from 0 to 1 into array pot_g_PotValues_f32 with length equal to potentiometer count (in our case 4). It also uses filtering, where each 10ms cycle we read a value to buffer, and use previous X number of readings (e.g. 50) to average the values. This gives us a low-pass filter which is what we want.

### EMG sensor inputs (SNS)

Similar to potentiometer inputs. The EMG sensor gives us analog voltage proportional to connected muscle activation. We also apply similar filtering and provide values same, values between 0 and 1 in array sns_g_ActiveStatus_u8 with length equal to number of sensors (for now 2).

### Servo motor outputs & control (SRV)

Servo module actually has some logic other than just writing value. It is still basic logic so it will be put here, but once the project is a bit more mature, we will add an 'application' layer to the project which will then actually handle the main 'abstract' logic and use the 'drivers' (from drivers folder) to actuate outputs and get inputs.

For now it works with 5 cases, all selectable by DIP switch bootstrap pins. Since we have 4 pins and combine them binary into a number, we can look at them as REV00, REV01, REV02, REV03 and REV04.

 - REV00: Sets servo angle to a value from a potentiometer
 - REV01: Sets servo angle to a value from a sensor
 - REV02: Sets servo to some angle if a button is pressed (min/max angle controlled by servo position)
 - REV03: Sets servo to some angle if a sensor threshold is activated (min/max angle controlled by servo position)
 - REV04: Sets servo PWM output from 0% duty to 100% duty (even if that is not a standard pot signal) based on potentiometer value

## Using the program

If serial degbug is enabled, the output to console for now looks like this:
```
----------------------------------------
 > runtimes (in microseconds):
    ├─[0] curr: 14, min: 13, max: 73
    ├─[1] curr: 715, min: 702, max: 843
    ├─[2] curr: 24, min: 23, max: 81
    ├─[3] curr: 1, min: 1, max: 1
    ├─[4] curr: 1, min: 1, max: 1
    ├─[5] curr: 1, min: 1, max: 1
    ├─[6] curr: 1, min: 1, max: 1
    ├─[7] curr: 1, min: 1, max: 1
    ├─[8] curr: 1, min: 1, max: 1
    ├─[9] curr: 1, min: 1, max: 1
btns:  0  0  0  0
pots:  179.96  30.22  0.00
servo working
```

Here we can see the above-mentioned 10 x 1ms tasks with each tasks current execution time, min and max times. Also each driver can implement its own serial debug function where it displays useful data to serial (button states, pot values, if servo driver is running...)
Hopefully we will soon update this to use json format, as it will then be easier to use with some other program on the PC for visualising the data.

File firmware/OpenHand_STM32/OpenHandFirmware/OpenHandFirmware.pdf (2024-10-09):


09/10/2024

## OpenHandFirmware Project Configuration Report

# 1. Description

## 1.1. Project

Project Name | OpenHandFirmware
Board Name | custom
Generated with: | STM32CubeMX 6.9.2
Date | 10/09/2024

## 1.2. MCU

MCU Series | STM32F1
MCU Line | STM32F103
MCU name | STM32F103RBTx
MCU Package | LQFP64
MCU Pin number | 64

## 1.3. Core(s) information

Core(s) | Arm Cortex-M3

# 2. Pinout Configuration


# 3. Pins Configuration

Pin Number LQFP64 | Pin Name (function after reset) | Pin Type | Alternate Function(s) | Label
1 | VBAT | Power
5 | PD0-OSC_IN | I/O | RCC_OSC_IN
6 | PD1-OSC_OUT | I/O | RCC_OSC_OUT
7 | NRST | Reset
12 | VSSA | Power
13 | VDDA | Power
18 | VSS | Power
19 | VDD | Power
25 | PC5 * | I/O | GPIO_Output | MOTOR_01_EN
27 | PB1 * | I/O | GPIO_Output | MOTOR_02_EN
29 | PB10 * | I/O | GPIO_Output | MOTOR_03_EN
31 | VSS | Power
32 | VDD | Power
38 | PC7 * | I/O | GPIO_Output | MOTOR_01_DIR
39 | PC8 | I/O | TIM3_CH3 | MOTOR_01_PWM
40 | PC9 * | I/O | GPIO_Output | MOTOR_02_DIR
41 | PA8 | I/O | TIM1_CH1 | MOTOR_02_PWM
42 | PA9 * | I/O | GPIO_Output | MOTOR_03_DIR
43 | PA10 | I/O | TIM1_CH3 | MOTOR_03_PWM
46 | PA13 | I/O | SYS_JTMS-SWDIO
47 | VSS | Power
48 | VDD | Power
49 | PA14 | I/O | SYS_JTCK-SWCLK
57 | PB5 * | I/O | GPIO_Output | LED_01
58 | PB6 * | I/O | GPIO_Output | LED_02
59 | PB7 * | I/O | GPIO_Input | BTN
60 | BOOT0 | Boot
63 | VSS | Power
64 | VDD | Power

## * The pin is affected with an I/O function

# 4. Clock Tree Configuration


# 5. Software Project

## 5.1. Project Settings

Name | Value
Project Name | OpenHandFirmware
Project Folder | C:\Users\aleksaheler\Documents\GitHub\ProstheticHand\firmware\OpenHand_S
Toolchain / IDE | STM32CubeIDE
Firmware Package Name and Version | STM32Cube FW_F1 V1.8.5
Application Structure | Advanced
Generate Under Root | Yes
Do not generate the main() | No
Minimum Heap Size | 0x200
Minimum Stack Size | 0x400

## 5.2. Code Generation Settings

Name | Value
STM32Cube MCU packages and embedded software | Copy only the necessary library files
Generate peripheral initialization as a pair of '.c/.h' files | No
Backup previously generated files when re-generating | No
Keep User Code when re-generating | Yes
Delete previously generated files when not re-generated | Yes
Set all free pins as analog (to optimize the power consumption) | No
Enable Full Assert | No

## 5.3. Advanced Settings - Generated Function Calls

Rank | Function Name | Peripheral Instance Name
1 | SystemClock_Config | RCC
2 | MX_GPIO_Init | GPIO
3 | MX_TIM1_Init | TIM1
4 | MX_TIM3_Init | TIM3

# 1. Power Consumption Calculator report

## 1.1. Microcontroller Selection

Series | STM32F1
Line | STM32F103
MCU | STM32F103RBTx
Datasheet | DS5319_Rev17

## 1.2. Parameter Selection

Temperature | 25
Vdd | 3.3

## 1.3. Battery Selection

Battery | Li-SOCL2(A3400)
Capacity | 3400.0 mAh
Self Discharge | 0.08 %/month
Nominal Voltage | 3.6 V
Max Cont Current | 100.0 mA
Max Pulse Current | 200.0 mA
Cells in series | 1
Cells in parallel | 1

## 1.4. Sequence

Step | Step1 | Step2
Mode | RUN | STOP
Vdd | 3.3 | 3.3
Voltage Source | Battery | Battery
Range | No Scale | No Scale
Fetch Type | FLASH | n/a
CPU Frequency | 72 MHz | 0 Hz
Clock Configuration | HSE PLL | Regulator_LP
Clock Source Frequency | 8 MHz | 0 Hz

### Peripherals

Additional Cons. | 0 mA | 0 mA
Average Current | 27 mA | 14 µA
Duration | 0.1 ms | 0.9 ms
DMIPS | 90.0 | 0.0
Ta Max | 100.99 | 105
Category | In DS Table | In DS Table

## 1.5. Results

Sequence Time | 1 ms | Average Current | 2.71 mA
Battery Life | 1 month, 21 days, 17 hours | Average DMIPS | 61.0 DMIPS

## 1.6. Chart


# 2. Peripherals and Middlewares Configuration

## 2.1. RCC High Speed Clock (HSE): Crystal/Ceramic Resonator

## 2.1.1. Parameter Settings:

### System Parameters:

VDD voltage (V) | 3.3
Prefetch Buffer | Enabled
Flash Latency(WS) | 2 WS (3 CPU cycle)

### RCC Parameters:

HSI Calibration Value | 16
HSE Startup Timout Value (ms) | 100
LSE Startup Timout Value (ms) | 5000

## 2.2. SYS Debug: Serial Wire Timebase Source: TIM4

## 2.3. TIM1 Channel1: PWM Generation CH1 Channel3: PWM Generation CH3

## 2.3.1. Parameter Settings:

### Counter Settings:

Prescaler (PSC - 16 bits value) | 72 *
Counter Mode | Up
Counter Period (AutoReload Register - 16 bits value ) | 20-1 *
Internal Clock Division (CKD) | No Division
Repetition Counter (RCR - 8 bits value) | 0
auto-reload preload | Enable *

### Trigger Output (TRGO) Parameters:

Master/Slave Mode (MSM bit) | Disable (Trigger input effect not delayed)
Trigger Event Selection | Reset (UG bit from TIMx_EGR)

### Break And Dead Time management - BRK Configuration:

BRK State | Disable
BRK Polarity | High

### Break And Dead Time management - Output Configuration:

Automatic Output State | Disable
Off State Selection for Run Mode (OSSR) | Disable
Off State Selection for Idle Mode (OSSI) | Disable
Lock Configuration | Off

### PWM Generation Channel 1:

Mode | PWM mode 1
Pulse (16 bits value) | 0
Output compare preload | Enable
Fast Mode | Disable
CH Polarity | High
CH Idle State | Reset

### PWM Generation Channel 3:

Mode | PWM mode 1
Pulse (16 bits value) | 0
Output compare preload | Enable
Fast Mode | Disable
CH Polarity | High
CH Idle State | Reset

## 2.4. TIM3 Channel3: PWM Generation CH3

## 2.4.1. Parameter Settings:

### Counter Settings:

Prescaler (PSC - 16 bits value) | 72 *
Counter Mode | Up
Counter Period (AutoReload Register - 16 bits value ) | 20-1 *
Internal Clock Division (CKD) | No Division
auto-reload preload | Enable *

### Trigger Output (TRGO) Parameters:

Master/Slave Mode (MSM bit) | Disable (Trigger input effect not delayed)
Trigger Event Selection | Reset (UG bit from TIMx_EGR)

### PWM Generation Channel 3:

Mode | PWM mode 1
Pulse (16 bits value) | 0
Output compare preload | Enable
Fast Mode | Disable
CH Polarity | High

## 2.5. FREERTOS Interface: CMSIS_V2

## 2.5.1. Config parameters:

### API:

FreeRTOS API | CMSIS v2

### Versions:

FreeRTOS version | 10.0.1
CMSIS-RTOS version | 2.00

### Kernel settings:

USE_PREEMPTION | Enabled
CPU_CLOCK_HZ | SystemCoreClock
TICK_RATE_HZ | 1000
MAX_PRIORITIES | 56
MINIMAL_STACK_SIZE | 128
MAX_TASK_NAME_LEN | 16
USE_16_BIT_TICKS | Disabled
IDLE_SHOULD_YIELD | Enabled
USE_MUTEXES | Enabled
USE_RECURSIVE_MUTEXES | Enabled
USE_COUNTING_SEMAPHORES | Enabled
QUEUE_REGISTRY_SIZE | 8
USE_APPLICATION_TASK_TAG | Disabled
ENABLE_BACKWARD_COMPATIBILITY | Enabled
USE_PORT_OPTIMISED_TASK_SELECTION | Disabled
USE_TICKLESS_IDLE | Disabled
USE_TASK_NOTIFICATIONS | Enabled
RECORD_STACK_HIGH_ADDRESS | Disabled

### Memory management settings:

Memory Allocation | Dynamic / Static
TOTAL_HEAP_SIZE | 3072
Memory Management scheme | heap_4

### Hook function related definitions:

USE_IDLE_HOOK | Disabled
USE_TICK_HOOK | Disabled
USE_MALLOC_FAILED_HOOK | Disabled
USE_DAEMON_TASK_STARTUP_HOOK | Disabled
CHECK_FOR_STACK_OVERFLOW | Disabled

### Run time and task stats gathering related definitions:

GENERATE_RUN_TIME_STATS | Disabled
USE_TRACE_FACILITY | Enabled
USE_STATS_FORMATTING_FUNCTIONS | Disabled

### Co-routine related definitions:

USE_CO_ROUTINES | Disabled
MAX_CO_ROUTINE_PRIORITIES | 2

### Software timer definitions:

USE_TIMERS | Enabled
TIMER_TASK_PRIORITY | 2
TIMER_QUEUE_LENGTH | 10
TIMER_TASK_STACK_DEPTH | 256

### Interrupt nesting behaviour configuration:

LIBRARY_LOWEST_INTERRUPT_PRIORITY | 15
LIBRARY_MAX_SYSCALL_INTERRUPT_PRIORITY | 5

## 2.5.2. Include parameters:

### Include definitions:

vTaskPrioritySet | Enabled
uxTaskPriorityGet | Enabled
vTaskDelete | Enabled
vTaskCleanUpResources | Disabled
vTaskSuspend | Enabled
vTaskDelayUntil | Enabled
vTaskDelay | Enabled
xTaskGetSchedulerState | Enabled
xTaskResumeFromISR | Enabled
xQueueGetMutexHolder | Enabled
xSemaphoreGetMutexHolder | Disabled
pcTaskGetTaskName | Disabled
uxTaskGetStackHighWaterMark | Enabled
xTaskGetCurrentTaskHandle | Disabled
eTaskGetState | Enabled
xEventGroupSetBitFromISR | Disabled
xTimerPendFunctionCall | Enabled
xTaskAbortDelay | Disabled
xTaskGetHandle | Disabled

## 2.5.3. Advanced settings:

### Newlib settings (see parameter description first):

USE_NEWLIB_REENTRANT | Enabled *

### Project settings (see parameter description first):

Use FW pack heap file | Enabled

### * User modified value

# 3. System Configuration

## 3.1. GPIO configuration

IP | Pin | Signal | GPIO mode | GPIO pull/up pull down | Max Speed | User Label
RCC | PD0-OSC_IN | RCC_OSC_IN | n/a | n/a | n/a
| PD1-OSC_OUT | RCC_OSC_OUT | n/a | n/a | n/a
SYS | PA13 | SYS_JTMS-SWDIO | n/a | n/a | n/a
| PA14 | SYS_JTCK-SWCLK | n/a | n/a | n/a
TIM1 | PA8 | TIM1_CH1 | Alternate Function Push Pull | n/a | Low | MOTOR_02_PWM
| PA10 | TIM1_CH3 | Alternate Function Push Pull | n/a | Low | MOTOR_03_PWM
TIM3 | PC8 | TIM3_CH3 | Alternate Function Push Pull | n/a | Low | MOTOR_01_PWM
GPIO | PC5 | GPIO_Output | Output Push Pull | No pull-up and no pull-down | Low | MOTOR_01_EN
| PB1 | GPIO_Output | Output Push Pull | No pull-up and no pull-down | Low | MOTOR_02_EN
| PB10 | GPIO_Output | Output Push Pull | No pull-up and no pull-down | Low | MOTOR_03_EN
| PC7 | GPIO_Output | Output Push Pull | No pull-up and no pull-down | Low | MOTOR_01_DIR
| PC9 | GPIO_Output | Output Push Pull | No pull-up and no pull-down | Low | MOTOR_02_DIR
| PA9 | GPIO_Output | Output Push Pull | No pull-up and no pull-down | Low | MOTOR_03_DIR
| PB5 | GPIO_Output | Output Push Pull | No pull-up and no pull-down | Low | LED_01
| PB6 | GPIO_Output | Output Push Pull | No pull-up and no pull-down | Low | LED_02
| PB7 | GPIO_Input | Input mode | No pull-up and no pull-down | n/a | BTN

## 3.2. DMA configuration

## nothing configured in DMA service

## 3.3. NVIC configuration

## 3.3.1. NVIC

Interrupt Table | Enable | Preenmption Priority | SubPriority
Non maskable interrupt | true | 0 | 0
Hard fault interrupt | true | 0 | 0
Memory management fault | true | 0 | 0
Prefetch fault, memory access fault | true | 0 | 0
Undefined instruction or illegal state | true | 0 | 0
System service call via SWI instruction | true | 0 | 0
Debug monitor | true | 0 | 0
Pendable request for system service | true | 15 | 0
System tick timer | true | 15 | 0
TIM4 global interrupt | true | 15 | 0
PVD interrupt through EXTI line 16 | unused
Flash global interrupt | unused
RCC global interrupt | unused
TIM1 break interrupt | unused
TIM1 update interrupt | unused
TIM1 trigger and commutation interrupts | unused
TIM1 capture compare interrupt | unused
TIM3 global interrupt | unused

## 3.3.2. NVIC Code generation

Enabled interrupt Table | Select for init sequence ordering | Generate IRQ handler | Call HAL handler
Non maskable interrupt | false | true | false
Hard fault interrupt | false | true | false
Memory management fault | false | true | false
Prefetch fault, memory access fault | false | true | false
Undefined instruction or illegal state | false | true | false
System service call via SWI instruction | false | false | false
Debug monitor | false | true | false
Pendable request for system service | false | false | false
System tick timer | false | false | true
TIM4 global interrupt | false | true | true

### * User modified value

# 4. System Views

## 4.1. Category view 4.1.1. Current


# 5. Docs & Resources

Type | Link

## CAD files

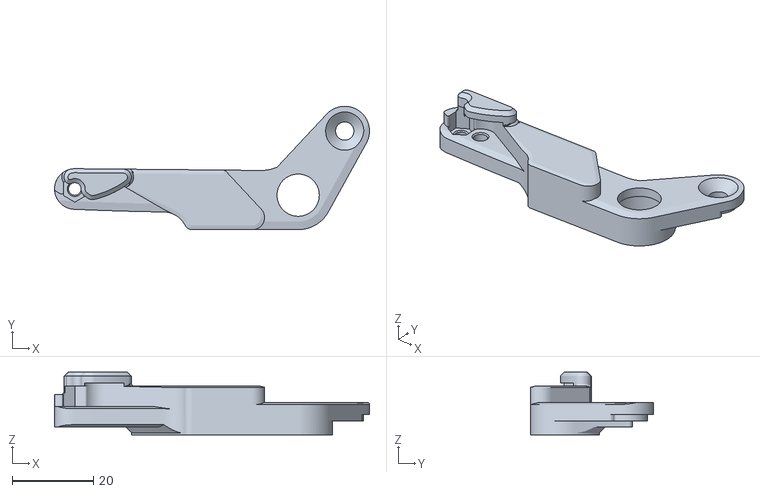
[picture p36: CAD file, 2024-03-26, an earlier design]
mechanical/old/hand_V1fingerDesign/proxyPhalanx.stl
77.5 x 30.4 x 15.5

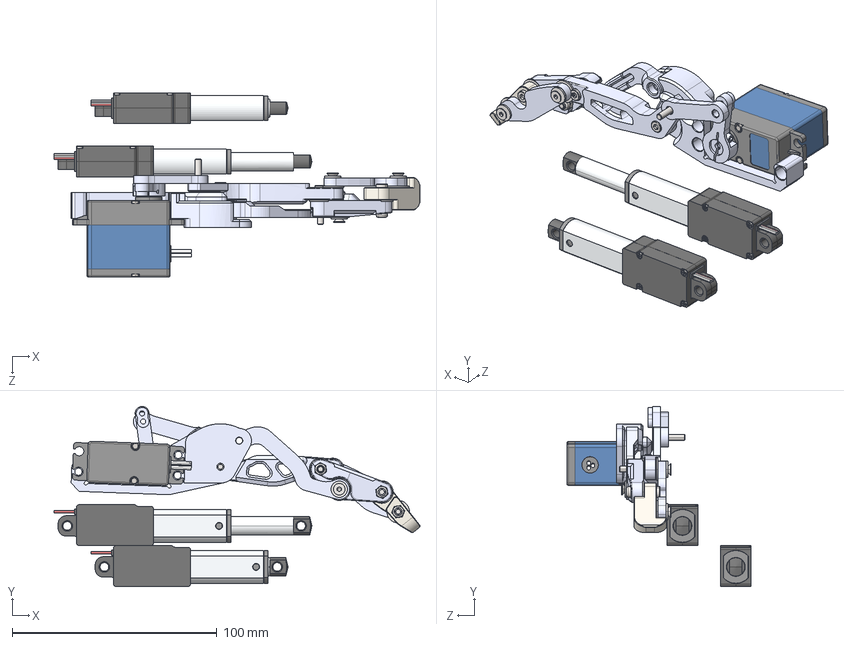
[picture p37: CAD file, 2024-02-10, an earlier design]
mechanical/old/OpenHandDesign/finger.step
178.9 x 88.1 x 90.1 mm
Copy of Part6^finger
Copy of Part7^finger
radial ball bearing_68_din_DIN 625 - 623 - 8,DE,NC,8_68
Copy of Part16^finger
prevailing torque nut style 1 insert_din_DIN EN ISO 7040 - M3 - N x 5
plain washer 6902 type abc_din_DIN 6902-B3.2 x 5
socket countersunk head screw_din_DIN 7991 - M3 x 16 --- 12.8N x 4
Copy of Part15^finger
plain washer 6902 type abc_din_DIN 6902-A3.2 x 4
socket head cap screw 4762_din_EN ISO 4762 M3 x 12 - 12N
socket head cap screw 4762_din_EN ISO 4762 M3 x 16 - 16N x 2
pushrod22
Part1^DC5821_master
Part4^finger
Copy of Part2^finger
linkServoFinger
Part1^LA-T8-6-30-3085-32 x 2
Part2^LA-T8-6-30-3085-32 x 2
Part3^LA-T8-6-30-3085-32 x 2
Part4^LA-T8-6-30-3085-32 x 2
Part5^LA-T8-6-30-3085-32 x 2

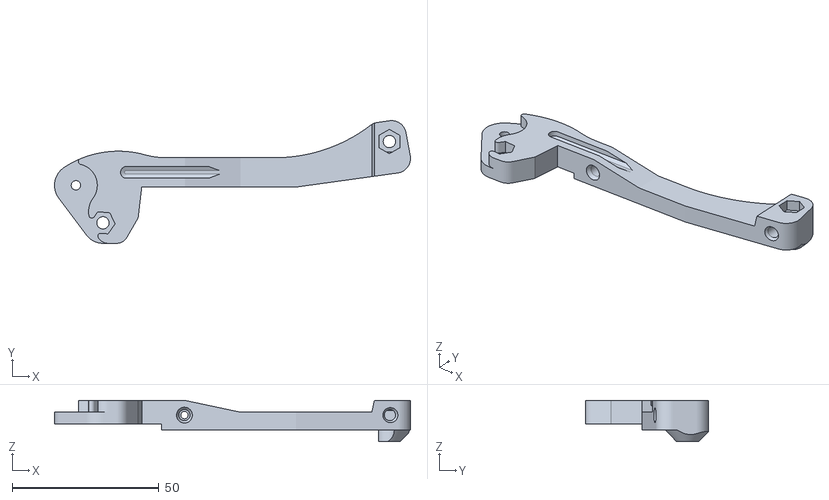
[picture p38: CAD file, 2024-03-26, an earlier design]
mechanical/old/hand_V1fingerDesign/fingerBase.stl
121.3 x 41.8 x 14.0

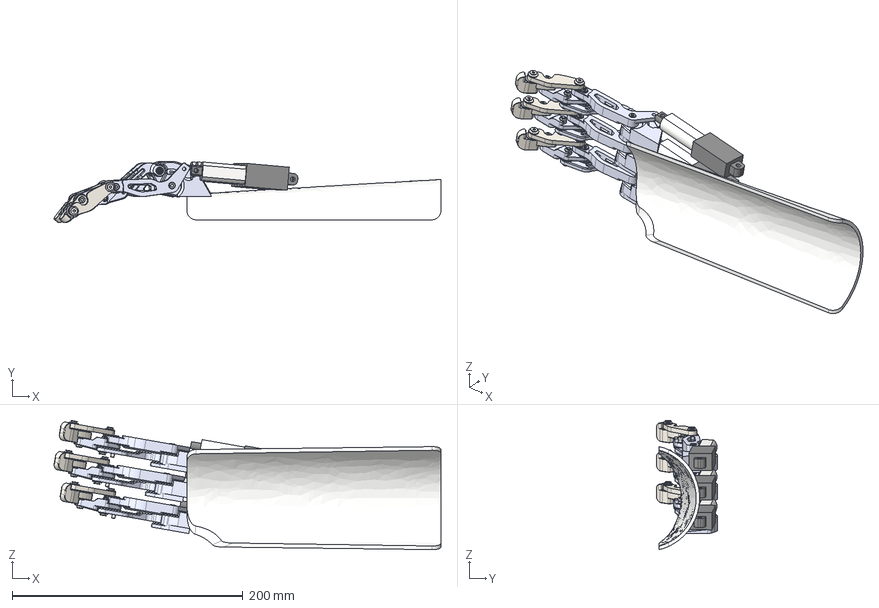
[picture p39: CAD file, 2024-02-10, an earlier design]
mechanical/old/OpenHandDesign/OpenHand.step
335.1 x 53.2 x 111.9 mm
Base
Motor x 3
Copy of Part6^finger x 3
Copy of Part7^finger x 3
radial ball bearing_68_din_DIN 625 - 623 - 8,DE,NC,8_68 x 3
Copy of Part16^finger x 3
prevailing torque nut style 1 insert_din_DIN EN ISO 7040 - M3 - N x 15
plain washer 6902 type abc_din_DIN 6902-B3.2 x 15
socket countersunk head screw_din_DIN 7991 - M3 x 16 --- 12.8N x 9
Copy of Part15^finger x 3
plain washer 6902 type abc_din_DIN 6902-A3.2 x 12
socket head cap screw 4762_din_EN ISO 4762 M3 x 12 - 12N x 3
socket head cap screw 4762_din_EN ISO 4762 M3 x 16 - 16N x 6
pushrod22 x 3
Part4^finger x 3

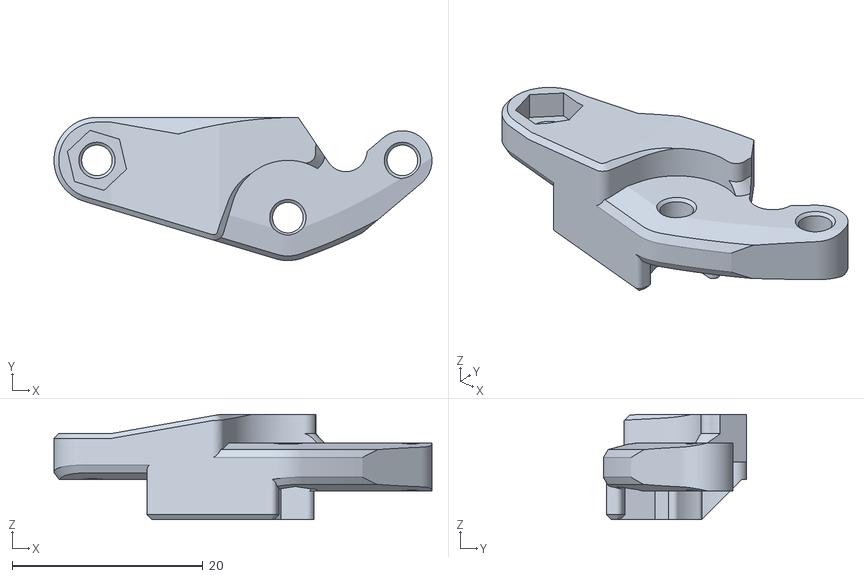
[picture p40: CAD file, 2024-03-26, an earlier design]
mechanical/old/hand_V1fingerDesign/part3.stl
39.6 x 15.0 x 11.0

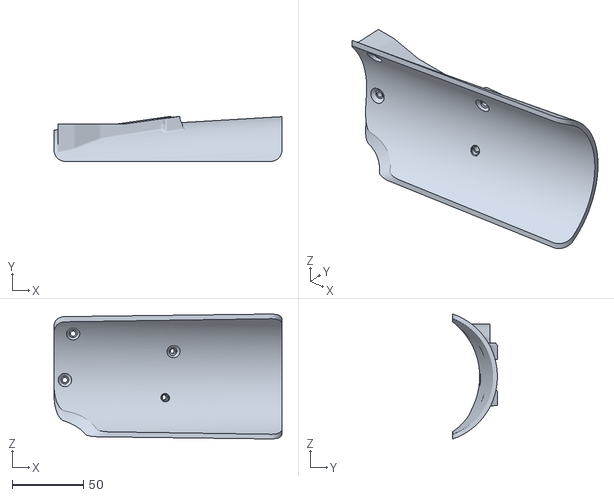
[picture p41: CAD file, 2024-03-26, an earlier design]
mechanical/old/hand_V1fingerDesign/base.stl
160.0 x 31.5 x 87.7

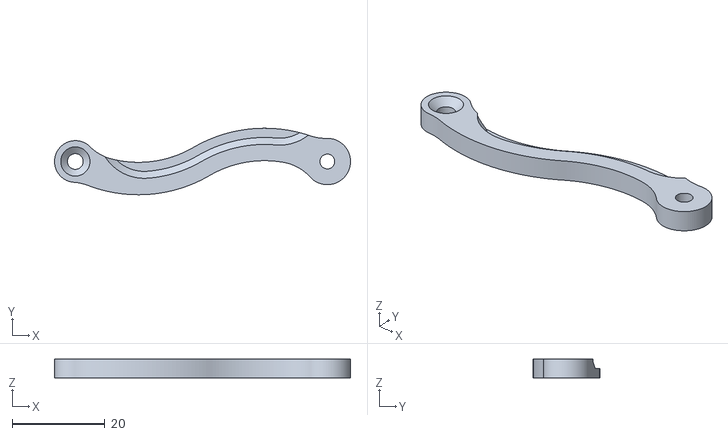
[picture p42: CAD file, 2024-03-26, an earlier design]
mechanical/old/hand_V1fingerDesign/part1.stl
63.9 x 14.4 x 4.00

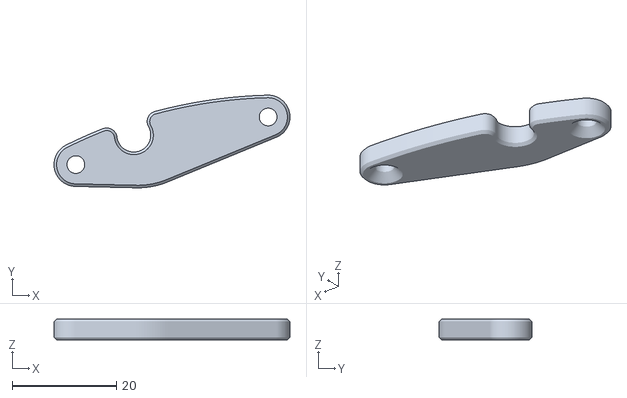
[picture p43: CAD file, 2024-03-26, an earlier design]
mechanical/old/hand_V1fingerDesign/postIntermediusPhalangealis.stl
45.4 x 17.8 x 4.00

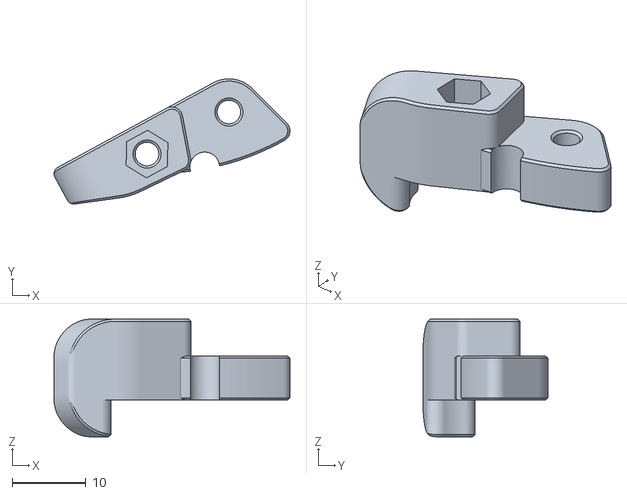
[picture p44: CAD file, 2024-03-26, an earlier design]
mechanical/old/hand_V1fingerDesign/fingerTip.stl
32.0 x 17.0 x 16.0

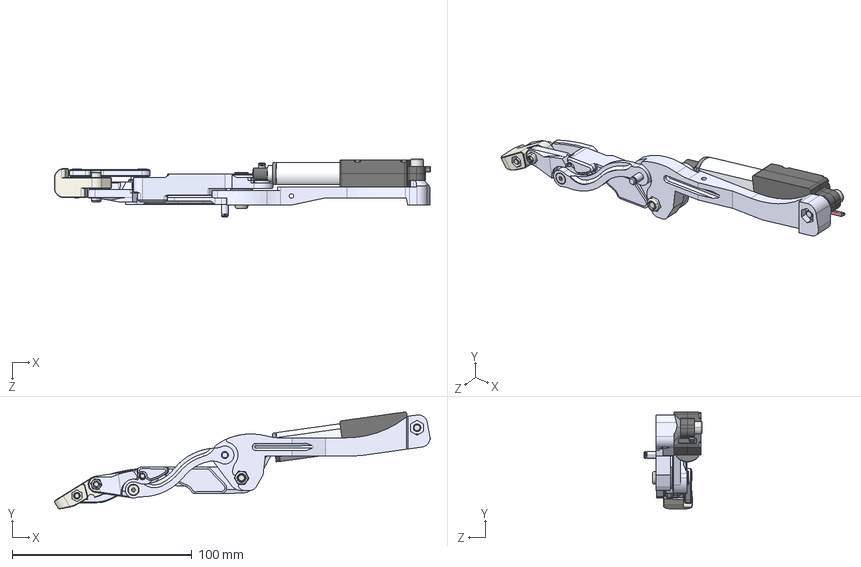
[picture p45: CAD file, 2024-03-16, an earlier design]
mechanical/old/hand_V1fingerDesign/ProstheticHand_V1_finger_rev0.61.STEP
208.9 x 53.9 x 32.1 mm
Part1^LA-T8-6-30-3085-32
Part2^LA-T8-6-30-3085-32
Part3^LA-T8-6-30-3085-32
Part5^LA-T8-6-30-3085-32
Part4^LA-T8-6-30-3085-32
radial ball bearing_68_din_DIN 625 - 624 - 8,DE,NC,8_68
flatHeadPin_M4x10 x 2
proxy_phalanx
plain washer 6902 type abc_din_DIN 6902-C3.6 x 5
plain washer 6902 type abc_din_DIN 6902-B3.6
Part1^master
fingerTIp_mirror
plain washer 6902 type abc_din_DIN 6902-A2.75 x 5
prevailing torque nut style 1 insert_din_DIN EN ISO 7040 - M3 - N x 3
prevailing torque nut style 1 insert_din_DIN EN ISO 7040 - M4 - N
socket head cap screw 4762_din_EN ISO 4762 M3 x 12 - 12N
postIntermediusPhalangealis
socket csink head cap screw 10642_din_EN ISO 10642 - M3 x 16 - 16N x 2
socket countersunk head screw_din_DIN 7991 - M3 x 16 --- 12.8N
socket countersunk head screw_din_DIN 7991 - M3 x 12 --- 8.8N
socket countersunk head screw_din_DIN 7991 - M4 x 20 --- 15.6N
socket head cap screw 4762_din_EN ISO 4762 M4 x 20 - 20N

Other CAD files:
mechanical/OpenHand/OpenHand Finger.f3d
mechanical/old/OpenHandDesign/OpenHand.f3d

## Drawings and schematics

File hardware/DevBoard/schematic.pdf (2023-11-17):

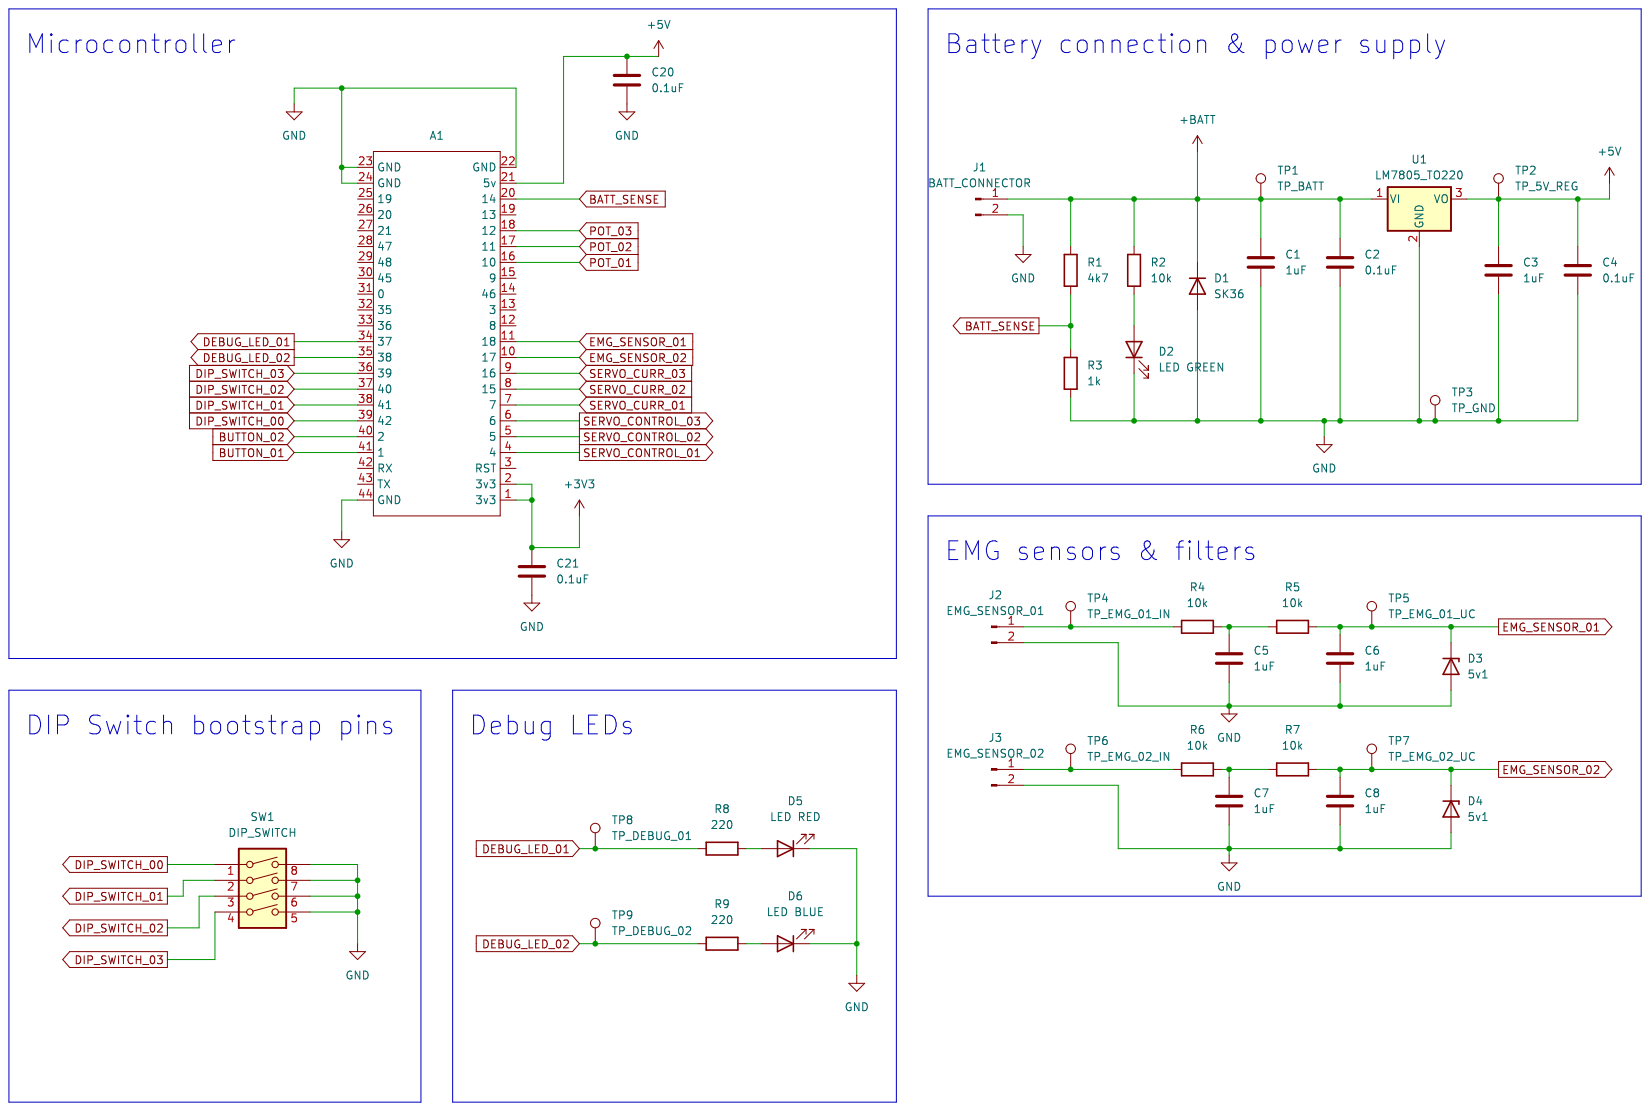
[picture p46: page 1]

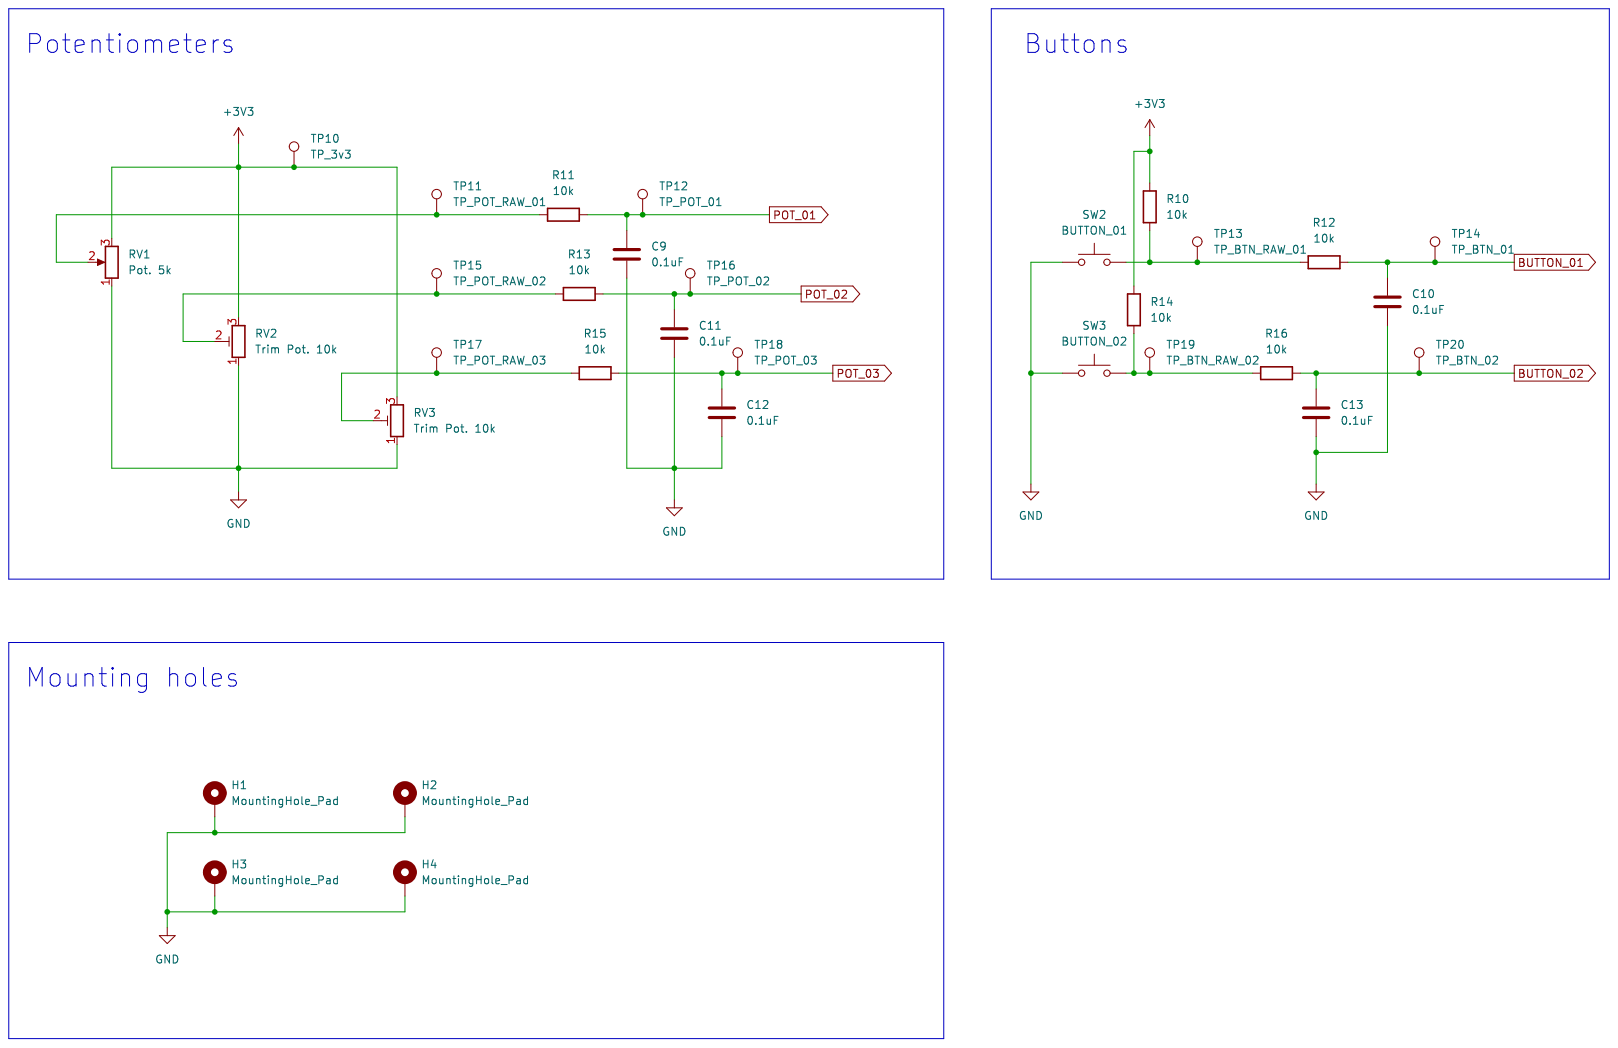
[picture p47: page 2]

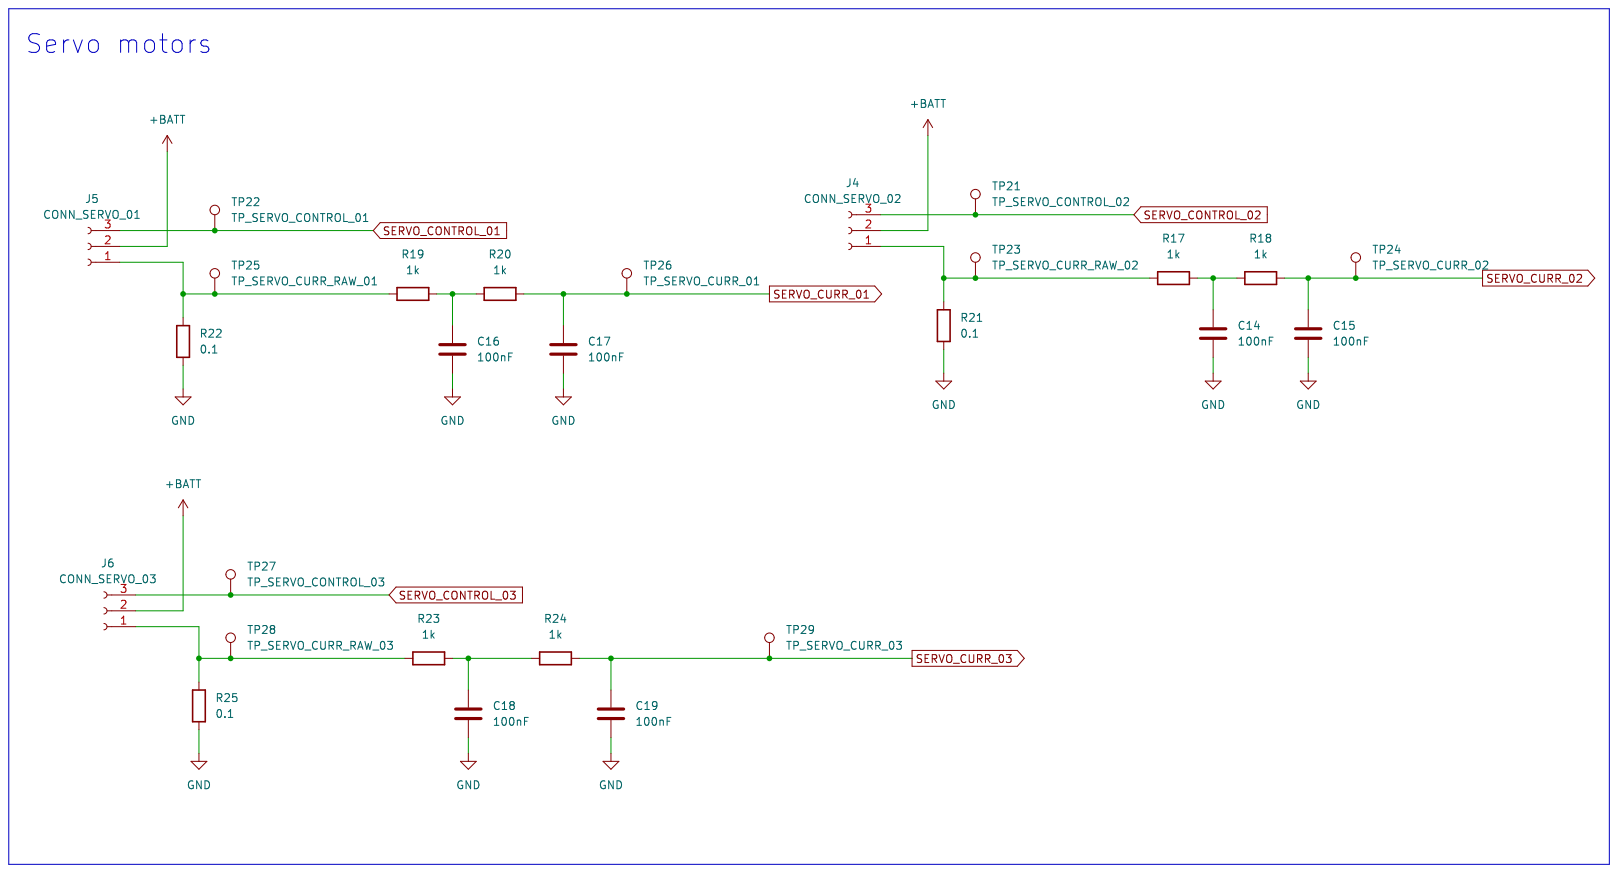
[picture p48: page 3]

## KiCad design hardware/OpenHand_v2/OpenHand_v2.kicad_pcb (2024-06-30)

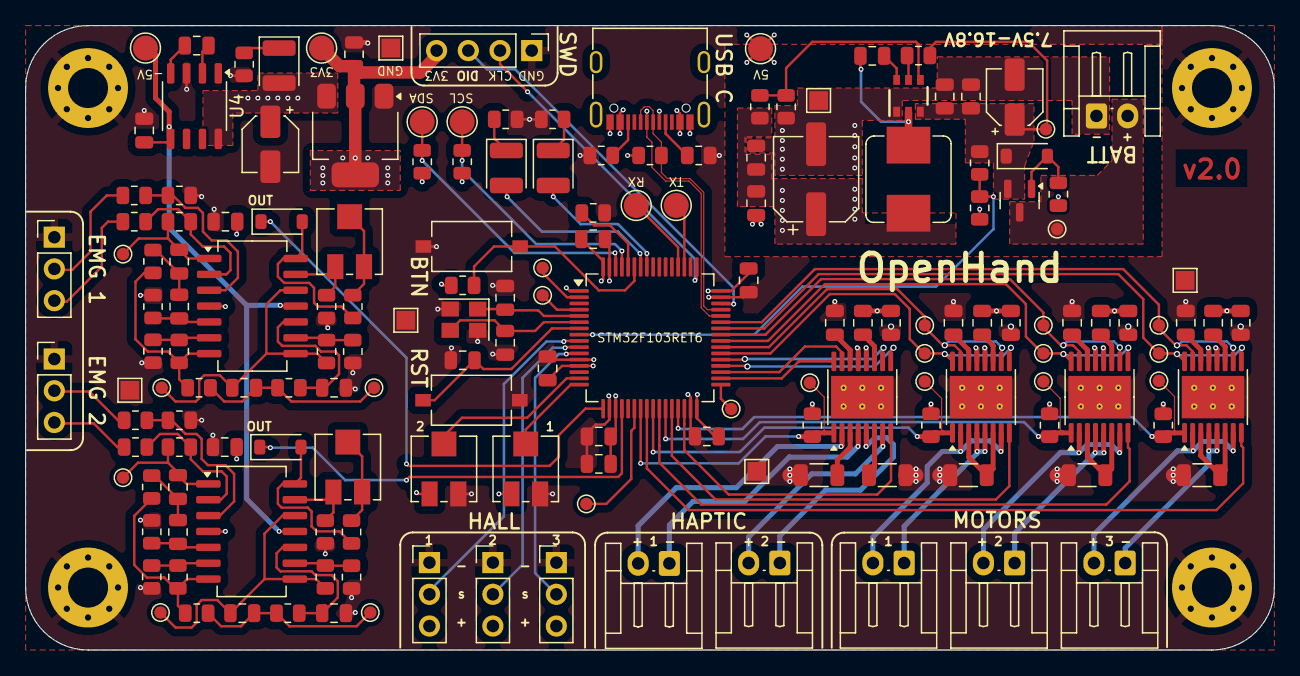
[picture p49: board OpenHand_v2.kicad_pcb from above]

Board: 4 copper layers, 100.0 x 50.0 mm, 172 parts (0 on the bottom side), 118 nets.

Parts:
C1, C2, C3, C4, C5, C6, C13, C21, C22: 100n; C_0805_2012Metric
C7, C12, C16: 1u; C_0805_2012Metric
C8, C9: 10p; C_0805_2012Metric
C10, C19: 10u; CP_Elec_4x5.4
C11, C17, C18, C20, C35, C36, C41, C42: 10u; C_0805_2012Metric
C14: 47u; CP_Elec_6.3x5.4
C15: 22u; C_0805_2012Metric
C23, C24, C25, C26: 470n; C_0805_2012Metric
C27, C28, C29, C30: 330n; C_0805_2012Metric
C31, C32, C37, C38: 2u2; C_0805_2012Metric
C33, C34, C39, C40: 10n; C_0805_2012Metric
D1, D4: RED; LED_1210_3225Metric
D2: GREEN; LED_1210_3225Metric
D3: 5V Zener; D_SOD-123
D5, D6: SS14; D_SOD-123
H1, H2, H3, H4: M3_Hole; MountingHole_3.2mm_M3_Pad_Via
J1: CONN_MOTOR_1; JST_EH_S2B-EH_1x02_P2.50mm_Horizontal
J2: CONN_MOTOR_2; JST_EH_S2B-EH_1x02_P2.50mm_Horizontal
J3: CONN_BATT; JST_EH_S2B-EH_1x02_P2.50mm_Horizontal
J4: CONN_POS_1; PinHeader_1x03_P2.54mm_Vertical
J5: CONN_USB_C; USB_C_Receptacle_G-Switch_GT-USB-7010ASV
J6: CONN_MOTOR_3; JST_EH_S2B-EH_1x02_P2.50mm_Horizontal
J7: CONN_FDBK_1; JST_EH_S2B-EH_1x02_P2.50mm_Horizontal
J8: CONN_EMG_1; PinHeader_1x03_P2.54mm_Vertical
J9: CONN_POS_2; PinHeader_1x03_P2.54mm_Vertical
J10: CONN_FDBK_2; JST_EH_S2B-EH_1x02_P2.50mm_Horizontal
J11: CONN_EMG_2; PinHeader_1x03_P2.54mm_Vertical
J12: CONN_SWD; PinHeader_1x04_P2.54mm_Vertical
J13: CONN_POS_3; PinHeader_1x03_P2.54mm_Vertical
L1: 3.3uH; L_Bourns_SRP7028A_7.3x6.6mm
Q1: AO3401A; SOT-23
R1, R2: 5k1; R_0805_2012Metric
R3: 1.5k; R_0805_2012Metric
R4, R5, R7, R15: 4k7; R_0805_2012Metric
R6, R8, R9, R11, R12, R16, R29, R32, R41, R42, R45, R46, R49, R50: 10k; R_0805_2012Metric
R10, R14, R17, R19, R27, R30, R37, R38: 47k; R_0805_2012Metric
R13: 54.9k; R_0805_2012Metric
R18, R20, R28, R31: 15k; R_0805_2012Metric
R21, R22, R23, R24, R25, R26, R35, R36, R39, R40: 1k; R_0805_2012Metric
R33, R34, R43, R44: 18k; R_0805_2012Metric
R47, R48, R52: 0R2; R_1206_3216Metric
R51, R53: 4R7; R_1206_3216Metric
RV1: TRIM_POT_1; Potentiometer_Vishay_TS53YJ_Vertical
RV2: TRIM_POT_2; Potentiometer_Vishay_TS53YJ_Vertical
RV3, RV4: 100k; Potentiometer_Vishay_TS53YJ_Vertical
SW1: BTN_RST; SW_Tactile_SPST_NO_Straight_CK_PTS636Sx25SMTRLFS
SW2: SW_Push; SW_Tactile_SPST_NO_Straight_CK_PTS636Sx25SMTRLFS
TP1: TP_UC_PA6; TestPoint_Pad_D1.0mm
TP2: TP_UC_TX; TestPoint_Pad_D2.0mm
TP3: TP_UC_RX; TestPoint_Pad_D2.0mm
TP4: TP_UC_PC13; TestPoint_Pad_D1.0mm
TP5: TP_UC_PC15; TestPoint_Pad_D1.0mm
TP6: TP_GND_1; TestPoint_Pad_1.5x1.5mm
TP7: TP_GND_2; TestPoint_Pad_1.5x1.5mm
TP8: TP_GND_3; TestPoint_Pad_1.5x1.5mm
TP9: TP_GND_4; TestPoint_Pad_1.5x1.5mm
TP10: TP_GND_5; TestPoint_Pad_1.5x1.5mm
TP11: TP_GND_6; TestPoint_Pad_1.5x1.5mm
TP12: TP_UC_SCL; TestPoint_Pad_D2.0mm
TP13: TP_UC_SDA; TestPoint_Pad_D2.0mm
TP14: TP_UC_PB12; TestPoint_Pad_D1.0mm
TP15: TP_BATT_P; TestPoint_Pad_D1.0mm
TP16: TP_V_BATT; TestPoint_Pad_D1.0mm
TP17: TP_V_5V; TestPoint_Pad_D2.0mm
TP18: TP_V_N5V; TestPoint_Pad_D2.0mm
TP19: TP_V_3V3; TestPoint_Pad_D2.0mm
TP20: TP_EMG_1_AMP; TestPoint_Pad_D1.0mm
TP21: TP_EMG_2_AMP; TestPoint_Pad_D1.0mm
TP22: TP_EMG_1_HP; TestPoint_Pad_D1.0mm
TP23: TP_EMG_2_HP; TestPoint_Pad_D1.0mm
TP24: TP_EMG_1_LP; TestPoint_Pad_D1.0mm
TP25: TP_EMG_2_LP; TestPoint_Pad_D1.0mm
TP26: TP_MOT_1_EN; TestPoint_Pad_D1.0mm
TP27: TP_MOT_2_EN; TestPoint_Pad_D1.0mm
TP28: TP_MOT_1_UC1; TestPoint_Pad_D1.0mm
TP29: TP_MOT_2_UC1; TestPoint_Pad_D1.0mm
TP30: TP_MOT_1_UC2; TestPoint_Pad_D1.0mm
TP31: TP_MOT_2_UC2; TestPoint_Pad_D1.0mm
TP32: TP_MOT_3_EN; TestPoint_Pad_D1.0mm
TP33: TP_FDBK_MOT_EN; TestPoint_Pad_D1.0mm
TP34: TP_MOT_3_UC1; TestPoint_Pad_D1.0mm
TP35: TP_MOT_3_UC2; TestPoint_Pad_D1.0mm
U1: STM32F103RETx; LQFP-64_10x10mm_P0.5mm
U2: TPS565201DDCR; TPS565201DDCR_L
U3: AMS1117-3.3; SOT-223-3_TabPin2
U4: ICL7660; SOP-8_3.9x4.9mm_P1.27mm
U5, U6: TL084; SO-14_5.3x10.2mm_P1.27mm
U7, U8, U9, U10: DRV8833PWP; HTSSOP-16-1EP_4.4x5mm_P0.65mm_EP3.4x5mm_Mask2.46x2.31mm_The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
Y1: 16MHz; Crystal_SMD_3225-4Pin_3.2x2.5mm

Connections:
+3V3: C2.1, C3.1, C4.1, C5.1, C6.1, C7.1, C18.1, J4.3, J9.3, J12.4, J13.3, R3.2, R4.2, R5.2, R6.1, RV1.3, RV2.3, TP19.1, U1.1 (VBAT), U1.13 (VDDA), U1.19 (VDD), U1.32 (VDD), U1.48 (VDD), U1.64 (VDD), U3.2 (VO)
+5V: C14.1, C15.1, C16.1, C19.1, C21.1, C22.1, C33.1, C34.1, C35.1, C36.1, C39.1, C40.1, C41.1, C42.1, D4.2 (A), J5.A4 (VBUS), J5.A9 (VBUS), J5.B4 (VBUS), J5.B9 (VBUS), L1.2, R13.1, R45.2, R46.2, R49.2, R50.2, TP17.1, U3.3 (VI), U4.8 (V+), U5.4 (V+), U6.4 (V+), U7.12 (VM), U8.12 (VM), U9.12 (VM), U10.12 (VM)
+BATT: C10.1, C11.1, C12.1, D3.1 (K), Q1.2 (S), R10.2, R12.2, TP16.1, U2.3 (VIN)
-5V: C17.1, TP18.1, U4.5 (VOUT), U5.11 (V-), U6.11 (V-)
/BATT_SENSE: R10.1, R11.2, U1.8 (PC0)
/HSE_IN: C8.1, U1.5 (PD0), Y1.1
/HSE_OUT: C9.1, U1.6 (PD1), Y1.3
/LED_1_K: D1.1 (K), R7.1
/LED_2_K: D2.1 (K), R8.1
/PSU/PSU_EN: R12.1, U2.5 (EN)
/PSU/PSU_LED_K: D4.1 (K), R15.1
/PSU/PSU_SW: C13.1, L1.1, U2.2 (SW)
/PSU/PSU_VBST: C13.2, U2.6 (VBST)
/PSU/PSU_VFB: R13.2, R16.1, U2.4 (VFB)
/PSU/REVP_MOS_GATE: D3.2 (A), Q1.1 (G), R14.2
/UC_BOOT: R9.2, U1.60 (BOOT0)
/USB_CC1: J5.A5 (CC1), R1.1
/USB_CC2: J5.B5 (CC2), R2.1
BAT_P: J3.2, Q1.3 (D), TP15.1
BTN_01: R6.2, SW2.1, U1.59 (PB7)
EMG_1_MIDPOINT: C27.1, R24.2, R35.1, TP22.1
EMG_01_N: J8.3, R23.2
EMG_01_P: J8.2, R21.2
EMG_01_UC: D5.1 (K), U1.17 (PA3)
EMG_2_MIDPOINT: C28.1, R26.2, R36.1, TP23.1
EMG_02_N: J11.3, R25.2
EMG_02_P: J11.2, R22.2
EMG_02_UC: D6.1 (K), U1.20 (PA4)
GND: C1.2, C2.2, C3.2, C4.2, C5.2, C6.2, C7.2, C8.2, C9.2, C10.2, C11.2, C12.2, C14.2, C15.2, C16.2, C17.2, C18.2, C19.2, C21.2, C22.2, C29.1, C30.1, C31.1, C32.1, C35.2, C36.2, C37.1, C38.1, C41.2, C42.2, H1.1, H2.1, H3.1, H4.1, J3.1, J4.1, J5.A1 (GND), J5.A12 (GND), J5.B1 (GND), J5.B12 (GND), J8.1, J9.1, J11.1, J12.1, J13.1, R1.2, R2.2, R7.2, R8.2, R9.1, R11.1, R14.1, R15.2, R16.2, R17.1, R19.1, R28.2, R31.2, R33.2, R34.2, R39.2, R40.2, R43.2, R44.2, R47.1, R48.1, R51.1, R52.1, R53.1, RV1.1, RV2.1, SW1.2, SW2.2, TP6.1, TP7.1, TP8.1, TP9.1, TP10.1, TP11.1, U1.12 (VSSA), U1.18 (VSS), U1.31 (VSS), U1.47 (VSS), U1.63 (VSS), U2.1 (GND), U3.1 (GND), U4.3 (GND), U7.13 (GND), U7.17 (GND), U8.13 (GND), U8.17 (GND), U9.13 (GND), U9.17 (GND), U10.13 (GND), U10.17 (GND), Y1.2, Y1.4
HALL_SENS_01_S: J4.2, U1.9 (PC1)
HALL_SENS_02_S: J9.2, U1.10 (PC2)
HALL_SENS_03_S: J13.2, U1.11 (PC3)
HAPTIC_01_DIR: U1.34 (PB13), U10.16 (AIN1)
HAPTIC_01_N: J7.1, U10.4 (AOUT2)
HAPTIC_01_P: J7.2, U10.2 (AOUT1)
HAPTIC_01_PWM: U1.35 (PB14), U10.15 (AIN2)
HAPTIC_02_DIR: U1.36 (PB15), U10.9 (BIN1)
HAPTIC_02_N: J10.1, U10.5 (BOUT2)
HAPTIC_02_P: J10.2, U10.7 (BOUT1)
HAPTIC_02_PWM: U1.37 (PC6), U10.10 (BIN2)
HAPTIC_EN: R50.1, TP33.1, U1.23 (PA7), U10.1 (~SLEEP)
HAPTIC_FAULT: U1.30 (PB11), U10.8 (~FAULT)
LED_1: D1.2 (A), U1.57 (PB5)
LED_2: D2.2 (A), U1.58 (PB6)
MOTOR_01_DIR: TP28.1, U1.38 (PC7), U7.9 (BIN1), U7.16 (AIN1)
MOTOR_01_EN: R45.1, TP26.1, U1.25 (PC5), U7.1 (~SLEEP)
MOTOR_01_FAULT: U1.28 (PB2), U7.8 (~FAULT)
MOTOR_01_N: J1.1, U7.4 (AOUT2), U7.5 (BOUT2)
MOTOR_01_P: J1.2, U7.2 (AOUT1), U7.7 (BOUT1)
MOTOR_01_PWM: TP30.1, U1.39 (PC8), U7.10 (BIN2), U7.15 (AIN2)
MOTOR_02_DIR: TP29.1, U1.40 (PC9), U8.9 (BIN1), U8.16 (AIN1)
MOTOR_02_EN: R46.1, TP27.1, U1.27 (PB1), U8.1 (~SLEEP)
MOTOR_02_FAULT: U1.26 (PB0), U8.8 (~FAULT)
MOTOR_02_N: J2.1, U8.4 (AOUT2), U8.5 (BOUT2)
MOTOR_02_P: J2.2, U8.2 (AOUT1), U8.7 (BOUT1)
MOTOR_02_PWM: TP31.1, U1.41 (PA8), U8.10 (BIN2), U8.15 (AIN2)
MOTOR_03_DIR: TP34.1, U1.42 (PA9), U9.9 (BIN1), U9.16 (AIN1)
MOTOR_03_EN: R49.1, TP32.1, U1.29 (PB10), U9.1 (~SLEEP)
MOTOR_03_FAULT: U1.24 (PC4), U9.8 (~FAULT)
MOTOR_03_N: J6.1, U9.4 (AOUT2), U9.5 (BOUT2)
MOTOR_03_P: J6.2, U9.2 (AOUT1), U9.7 (BOUT1)
MOTOR_03_PWM: TP35.1, U1.43 (PA10), U9.10 (BIN2), U9.15 (AIN2)
unnamed: C23.1, R27.2, TP20.1, U5.1
unnamed: C23.2, C24.1, R18.1
unnamed: C25.1, R30.2, TP21.1, U6.1
unnamed: C25.2, C26.1, R20.1
unnamed: D5.2 (A), R38.1, U5.14
unnamed: D6.2 (A), R37.1, U6.14
unnamed: R18.2, R24.1, R29.2, U5.7
unnamed: R20.2, R26.1, R32.2, U6.7
unnamed: R37.2, RV4.1, RV4.2
unnamed: R38.2, RV3.1, RV3.2
unnamed: TP1.1, U1.22 (PA6)
unnamed: TP14.1, U1.33 (PB12)
unnamed: TP4.1, U1.2 (PC13)
unnamed: TP5.1, U1.4 (PC15)
unnamed: C20.1, U4.2 (CAP+)
unnamed: C20.2, U4.4 (CAP-)
unnamed: R17.2, R21.1, U5.3 (+)
unnamed: R23.1, R27.1, U5.2 (-)
unnamed: C24.2, R28.1, U5.5 (+)
unnamed: R29.1, R33.1, U5.6 (-)
unnamed: C29.2, R35.2, U5.10 (+)
unnamed: R41.1, R43.1, U5.9 (-)
unnamed: C27.2, R41.2, TP24.1, U5.8, U5.12 (+)
unnamed: R39.1, RV3.3, U5.13 (-)
unnamed: R19.2, R22.1, U6.3 (+)
unnamed: R25.1, R30.1, U6.2 (-)
unnamed: C26.2, R31.1, U6.5 (+)
unnamed: R32.1, R34.1, U6.6 (-)
unnamed: C30.2, R36.2, U6.10 (+)
unnamed: R42.1, R44.1, U6.9 (-)
unnamed: C28.2, R42.2, TP25.1, U6.8, U6.12 (+)
unnamed: R40.1, RV4.3, U6.13 (-)
unnamed: R47.2, U7.3 (AISEN), U7.6 (BISEN)
unnamed: C33.2, U7.11 (VCP)
unnamed: C31.2, U7.14 (VINT)
unnamed: R48.2, U8.3 (AISEN), U8.6 (BISEN)
unnamed: C34.2, U8.11 (VCP)
unnamed: C32.2, U8.14 (VINT)
unnamed: R52.2, U9.3 (AISEN), U9.6 (BISEN)
unnamed: C39.2, U9.11 (VCP)
unnamed: C37.2, U9.14 (VINT)
unnamed: R51.2, U10.3 (AISEN)
unnamed: R53.2, U10.6 (BISEN)
unnamed: C40.2, U10.11 (VCP)
unnamed: C38.2, U10.14 (VINT)
SWCLK: J12.2, U1.49 (PA14)
SWDIO: J12.3, U1.46 (PA13)
TRIM_POT_01: RV1.2, U1.16 (PA2)
TRIM_POT_02: RV2.2, U1.15 (PA1)
UC_RST: C1.1, SW1.1, U1.7 (NRST)
UC_RX: TP3.1, U1.52 (PC11)
UC_SCL: R5.1, TP12.1, U1.61 (PB8)
UC_SDA: R4.1, TP13.1, U1.62 (PB9)
UC_TX: TP2.1, U1.51 (PC10)
USB_D+: J5.A6 (D+), J5.B6 (D+), R3.1, U1.45 (PA12)
USB_D-: J5.A7 (D-), J5.B7 (D-), U1.44 (PA11)

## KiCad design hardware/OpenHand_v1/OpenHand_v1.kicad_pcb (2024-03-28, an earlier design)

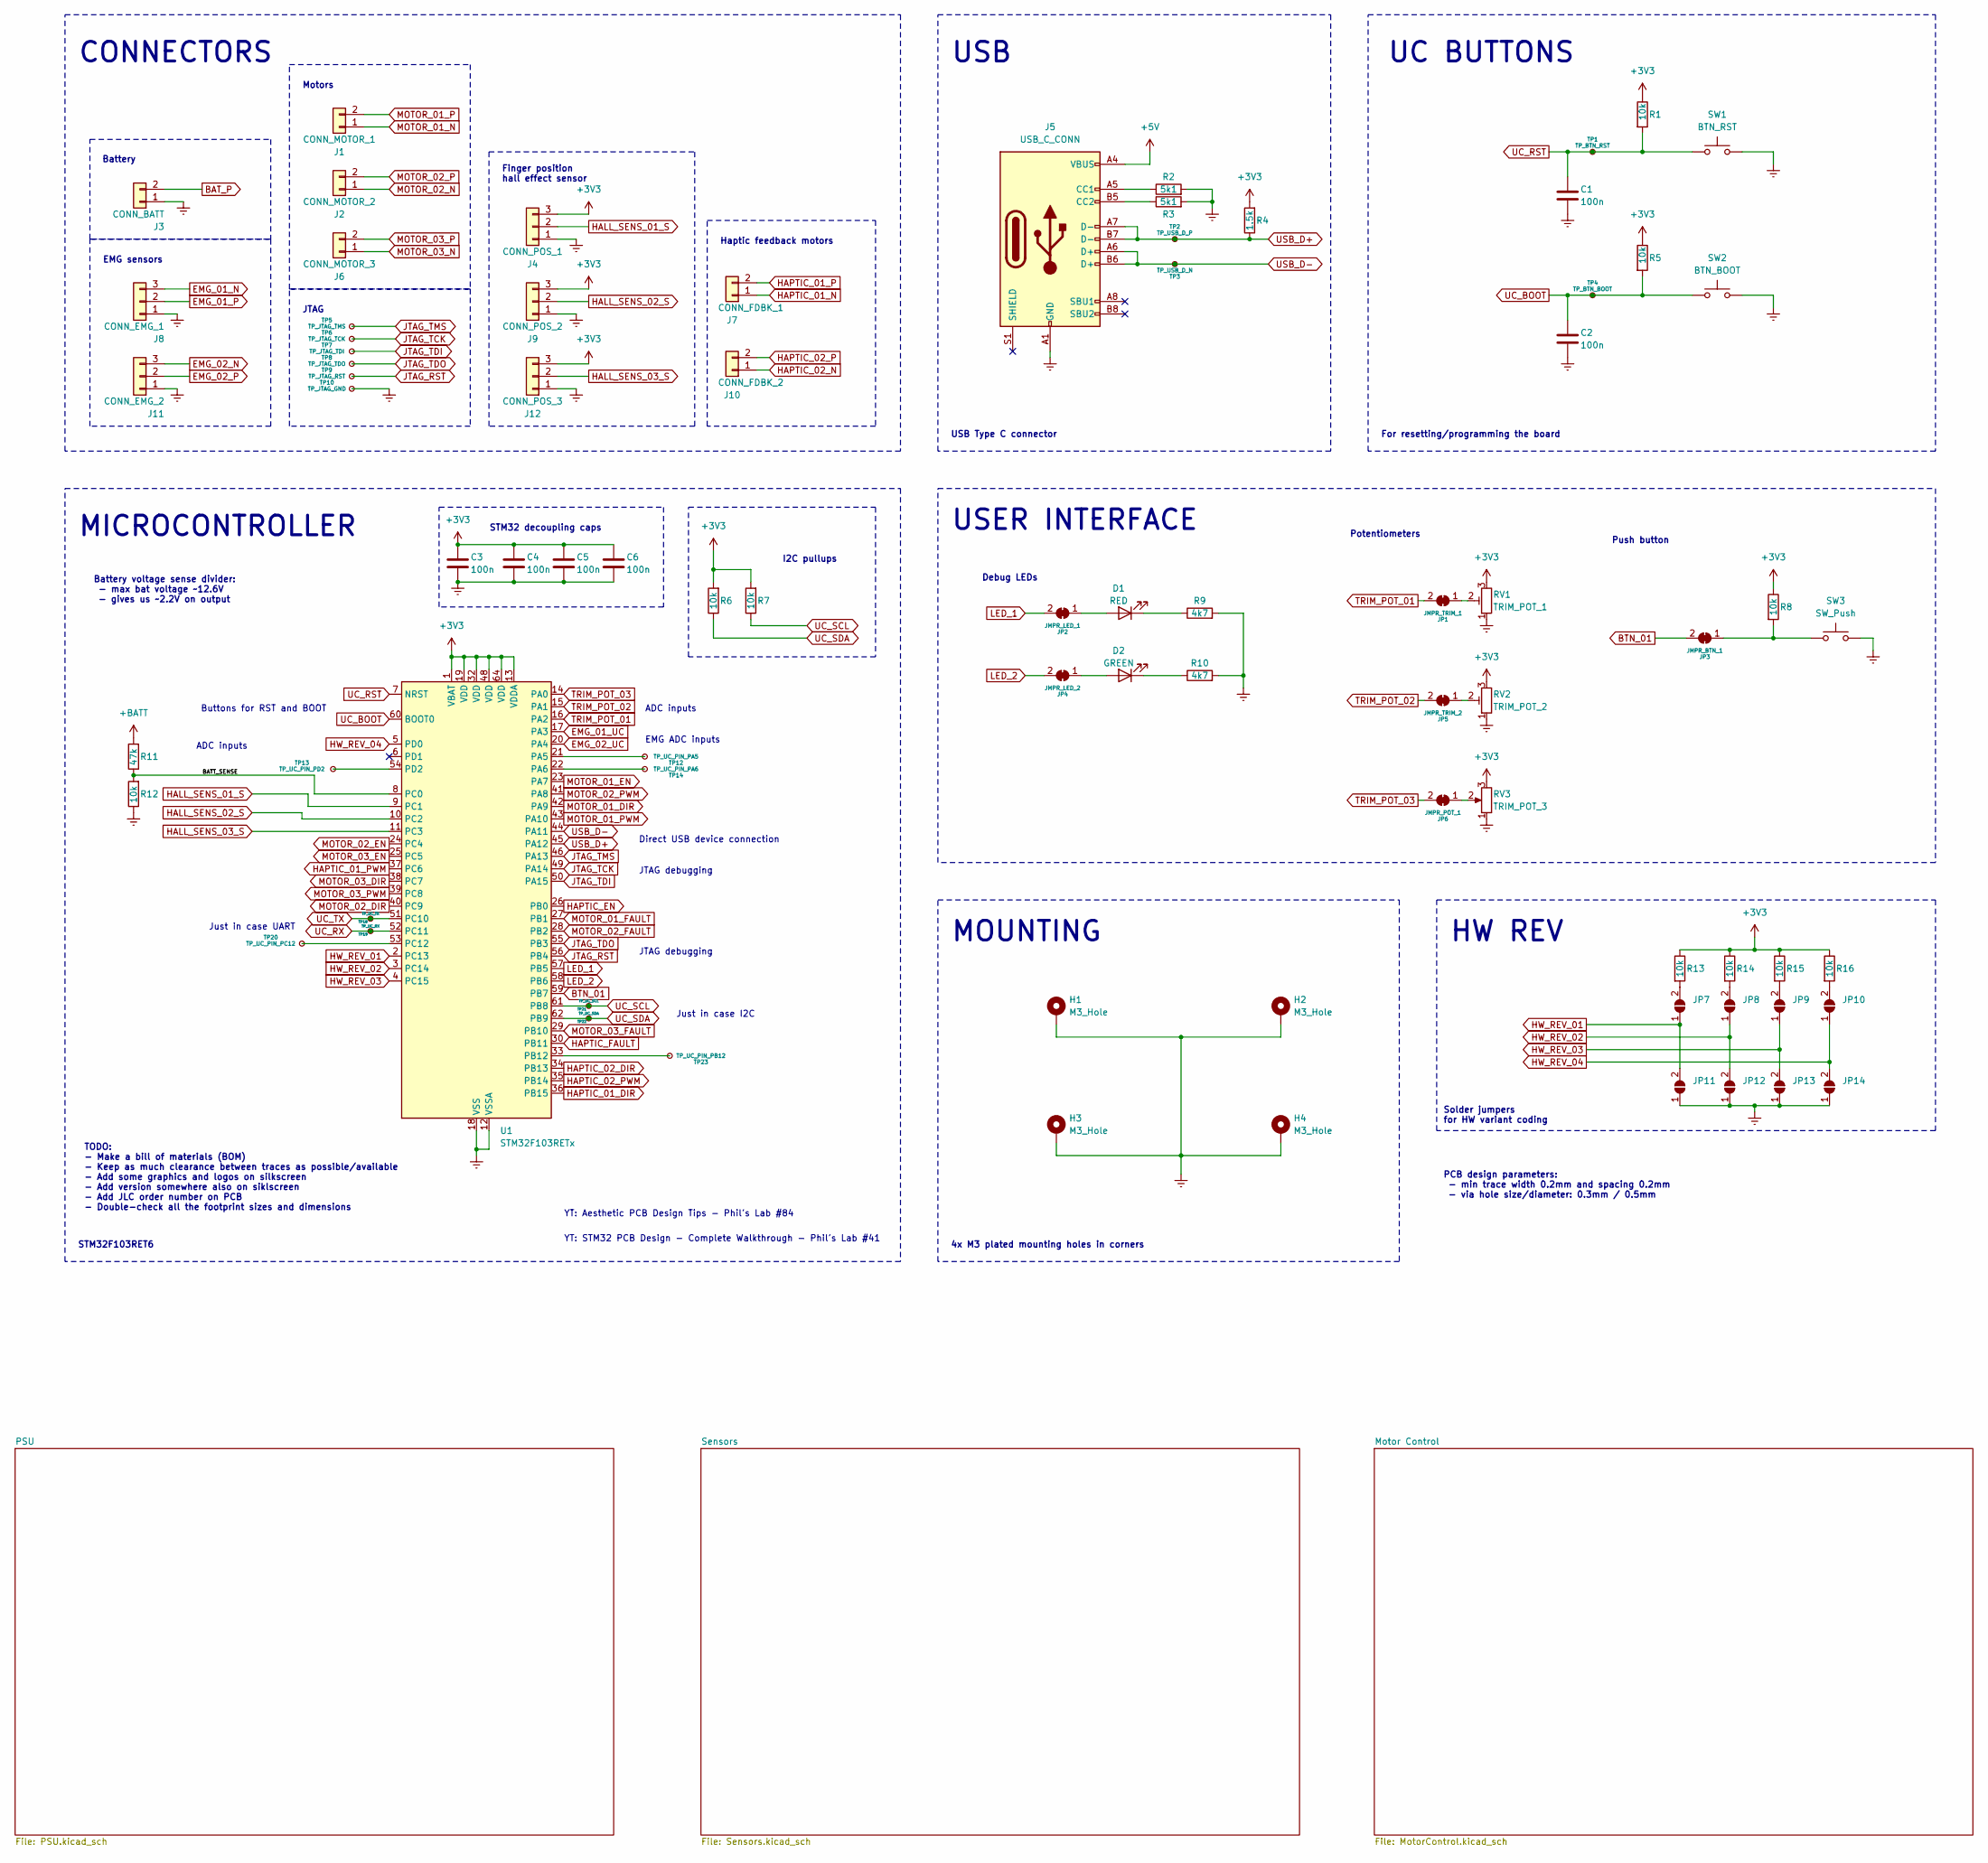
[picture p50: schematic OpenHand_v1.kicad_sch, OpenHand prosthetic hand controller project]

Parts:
C1, C2, C3, C4, C5, C6: 100n; C_0805_2012Metric
D1: RED; LED_1210_3225Metric
D2: GREEN; LED_1210_3225Metric
H1, H2, H3, H4: M3_Hole; MountingHole_3.2mm_M3_Pad_Via
J1: CONN_MOTOR_1; JST_EH_S2B-EH_1x02_P2.50mm_Horizontal
J2: CONN_MOTOR_2; JST_EH_S2B-EH_1x02_P2.50mm_Horizontal
J3: CONN_BATT; JST_EH_S2B-EH_1x02_P2.50mm_Horizontal
J4: CONN_POS_1; JST_EH_S3B-EH_1x03_P2.50mm_Horizontal
J5: USB_C_CONN; USB_C_Receptacle_G-Switch_GT-USB-7010ASV
J6: CONN_MOTOR_3; JST_EH_S2B-EH_1x02_P2.50mm_Horizontal
J7: CONN_FDBK_1; JST_EH_S2B-EH_1x02_P2.50mm_Horizontal
J8: CONN_EMG_1; JST_EH_S3B-EH_1x03_P2.50mm_Horizontal
J9: CONN_POS_2; JST_EH_S3B-EH_1x03_P2.50mm_Horizontal
J10: CONN_FDBK_2; JST_EH_S2B-EH_1x02_P2.50mm_Horizontal
J11: CONN_EMG_2; JST_EH_S3B-EH_1x03_P2.50mm_Horizontal
J12: CONN_POS_3; JST_EH_S3B-EH_1x03_P2.50mm_Horizontal
JP1: JMPR_TRIM_1; SolderJumper-2_P1.3mm_Bridged_RoundedPad1.0x1.5mm
JP2: JMPR_LED_1; SolderJumper-2_P1.3mm_Bridged_RoundedPad1.0x1.5mm
JP3: JMPR_BTN_1; SolderJumper-2_P1.3mm_Bridged_RoundedPad1.0x1.5mm
JP4: JMPR_LED_2; SolderJumper-2_P1.3mm_Bridged_RoundedPad1.0x1.5mm
JP5: JMPR_TRIM_2; SolderJumper-2_P1.3mm_Bridged_RoundedPad1.0x1.5mm
JP6: JMPR_POT_1; SolderJumper-2_P1.3mm_Bridged_RoundedPad1.0x1.5mm
JP7, JP8, JP9, JP10, JP11, JP12, JP13, JP14: SolderJumper_2_Open; SolderJumper-2_P1.3mm_Open_RoundedPad1.0x1.5mm
R1, R5, R6, R7, R8, R12, R13, R14, R15, R16: 10k; R_0805_2012Metric
R2, R3: 5k1; R_0805_2012Metric
R4: 1.5k; R_0805_2012Metric
R9, R10: 4k7; R_0805_2012Metric
R11: 47k; R_0805_2012Metric
RV1: TRIM_POT_1; Potentiometer_Vishay_TS53YJ_Vertical
RV2: TRIM_POT_2; Potentiometer_Vishay_TS53YJ_Vertical
RV3: TRIM_POT_3; Potentiometer_Vishay_TS53YJ_Vertical
SW1: BTN_RST; SW_Tactile_SPST_NO_Straight_CK_PTS636Sx25SMTRLFS
SW2: BTN_BOOT; SW_Tactile_SPST_NO_Straight_CK_PTS636Sx25SMTRLFS
SW3: SW_Push; SW_Tactile_SPST_NO_Straight_CK_PTS636Sx25SMTRLFS
TP1: TP_BTN_RST; TestPoint_Pad_D1.0mm
TP2: TP_USB_D_P; TestPoint_Pad_D1.0mm
TP3: TP_USB_D_N; TestPoint_Pad_D1.0mm
TP4: TP_BTN_BOOT; TestPoint_Pad_D1.0mm
TP5: TP_JTAG_TMS; TestPoint_Pad_D1.0mm
TP6: TP_JTAG_TCK; TestPoint_Pad_D1.0mm
TP7: TP_JTAG_TDI; TestPoint_Pad_D1.0mm
TP8: TP_JTAG_TDO; TestPoint_Pad_D1.0mm
TP9: TP_JTAG_RST; TestPoint_Pad_D1.0mm
TP10: TP_JTAG_GND; TestPoint_Pad_D1.0mm
TP12: TP_UC_PIN_PA5; TestPoint_Pad_D1.0mm
TP13: TP_UC_PIN_PD2; TestPoint_Pad_D1.0mm
TP14: TP_UC_PIN_PA6; TestPoint_Pad_D1.0mm
TP18: TP_UC_TX; TestPoint_Pad_D1.0mm
TP19: TP_UC_RX; TestPoint_Pad_D1.0mm
TP20: TP_UC_PIN_PC12; TestPoint_Pad_D1.0mm
TP21: TP_UC_SCL; TestPoint_Pad_D1.0mm
TP22: TP_UC_SDA; TestPoint_Pad_D1.0mm
TP23: TP_UC_PIN_PB12; TestPoint_Pad_D1.0mm
U1: STM32F103RETx; LQFP-64_10x10mm_P0.5mm

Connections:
+3V3: C3.1, C4.1, C5.1, C6.1, J4.3, J9.3, J12.3, R1.1, R4.2, R5.1, R6.2, R7.2, R8.1, R13.1, R14.1, R15.1, R16.1, RV1.3, RV2.3, RV3.3, U1.1 (VBAT), U1.13 (VDDA), U1.19 (VDD), U1.32 (VDD), U1.48 (VDD), U1.64 (VDD); also elsewhere on the board
+5V: J5.A4 (VBUS), J5.A9 (VBUS), J5.B4 (VBUS), J5.B9 (VBUS); also elsewhere on the board
+BATT: R11.2; also elsewhere on the board
/BATT_SENSE: R11.1, R12.2, U1.8 (PC0)
BAT_P: J3.2; also elsewhere on the board
BTN_01: JP3.2 (B), U1.59 (PB7)
EMG_01_N: J8.3; also elsewhere on the board
EMG_01_P: J8.2; also elsewhere on the board
EMG_01_UC: U1.17 (PA3); also elsewhere on the board
EMG_02_N: J11.3; also elsewhere on the board
EMG_02_P: J11.2; also elsewhere on the board
EMG_02_UC: U1.20 (PA4); also elsewhere on the board
Earth: C1.2, C2.2, C3.2, C4.2, C5.2, C6.2, H1.1, H2.1, H3.1, H4.1, J3.1, J4.1, J5.A1 (GND), J5.A12 (GND), J5.B1 (GND), J5.B12 (GND), J8.1, J9.1, J11.1, J12.1, JP11.1 (A), JP12.1 (A), JP13.1 (A), JP14.1 (A), R2.2, R3.2, R9.2, R10.2, R12.1, RV1.1, RV2.1, RV3.1, SW1.2, SW2.2, SW3.2, TP10.1, U1.12 (VSSA), U1.18 (VSS), U1.31 (VSS), U1.47 (VSS), U1.63 (VSS); also elsewhere on the board
HALL_SENS_01_S: J4.2, U1.9 (PC1)
HALL_SENS_02_S: J9.2, U1.10 (PC2)
HALL_SENS_03_S: J12.2, U1.11 (PC3)
HAPTIC_01_DIR: U1.36 (PB15); also elsewhere on the board
HAPTIC_01_N: J7.1; also elsewhere on the board
HAPTIC_01_P: J7.2; also elsewhere on the board
HAPTIC_01_PWM: U1.37 (PC6); also elsewhere on the board
HAPTIC_02_DIR: U1.34 (PB13); also elsewhere on the board
HAPTIC_02_N: J10.1; also elsewhere on the board
HAPTIC_02_P: J10.2; also elsewhere on the board
HAPTIC_02_PWM: U1.35 (PB14); also elsewhere on the board
HAPTIC_EN: U1.26 (PB0); also elsewhere on the board
HAPTIC_FAULT: U1.30 (PB11); also elsewhere on the board
HW_REV_01: JP7.1 (A), JP11.2 (B), U1.2 (PC13)
HW_REV_02: JP8.1 (A), JP12.2 (B), U1.3 (PC14)
HW_REV_03: JP9.1 (A), JP13.2 (B), U1.4 (PC15)
HW_REV_04: JP10.1 (A), JP14.2 (B), U1.5 (PD0)
JTAG_RST: TP9.1, U1.56 (PB4)
JTAG_TCK: TP6.1, U1.49 (PA14)
JTAG_TDI: TP7.1, U1.50 (PA15)
JTAG_TDO: TP8.1, U1.55 (PB3)
JTAG_TMS: TP5.1, U1.46 (PA13)
LED_1: JP2.2 (B), U1.57 (PB5)
LED_2: JP4.2 (B), U1.58 (PB6)
MOTOR_01_DIR: U1.42 (PA9); also elsewhere on the board
MOTOR_01_EN: U1.23 (PA7); also elsewhere on the board
MOTOR_01_FAULT: U1.27 (PB1); also elsewhere on the board
MOTOR_01_N: J1.1; also elsewhere on the board
MOTOR_01_P: J1.2; also elsewhere on the board
MOTOR_01_PWM: U1.43 (PA10); also elsewhere on the board
MOTOR_02_DIR: U1.40 (PC9); also elsewhere on the board
MOTOR_02_EN: U1.24 (PC4); also elsewhere on the board
MOTOR_02_FAULT: U1.28 (PB2); also elsewhere on the board
MOTOR_02_N: J2.1; also elsewhere on the board
MOTOR_02_P: J2.2; also elsewhere on the board
MOTOR_02_PWM: U1.41 (PA8); also elsewhere on the board
MOTOR_03_DIR: U1.38 (PC7); also elsewhere on the board
MOTOR_03_EN: U1.25 (PC5); also elsewhere on the board
MOTOR_03_FAULT: U1.29 (PB10); also elsewhere on the board
MOTOR_03_N: J6.1; also elsewhere on the board
MOTOR_03_P: J6.2; also elsewhere on the board
MOTOR_03_PWM: U1.39 (PC8); also elsewhere on the board
unnamed: D1.2 (A), JP2.1 (A)
unnamed: D1.1 (K), R9.1
unnamed: D2.2 (A), JP4.1 (A)
unnamed: D2.1 (K), R10.1
unnamed: J5.A5 (CC1), R2.1
unnamed: J5.B5 (CC2), R3.1
unnamed: JP1.1 (A), RV1.2
unnamed: JP3.1 (A), R8.2, SW3.1
unnamed: JP5.1 (A), RV2.2
unnamed: JP6.1 (A), RV3.2
unnamed: JP7.2 (B), R13.2
unnamed: JP8.2 (B), R14.2
unnamed: JP9.2 (B), R15.2
unnamed: JP10.2 (B), R16.2
unnamed: TP12.1, U1.21 (PA5)
unnamed: TP14.1, U1.22 (PA6)
unnamed: TP23.1, U1.33 (PB12)
unnamed: TP20.1, U1.53 (PC12)
unnamed: TP13.1, U1.54 (PD2)
TRIM_POT_01: JP1.2 (B), U1.16 (PA2)
TRIM_POT_02: JP5.2 (B), U1.15 (PA1)
TRIM_POT_03: JP6.2 (B), U1.14 (PA0)
UC_BOOT: C2.1, R5.2, SW2.1, TP4.1, U1.60 (BOOT0)
UC_RST: C1.1, R1.2, SW1.1, TP1.1, U1.7 (NRST)
UC_RX: TP19.1, U1.52 (PC11)
UC_SCL: R7.1, TP21.1, U1.61 (PB8)
UC_SDA: R6.1, TP22.1, U1.62 (PB9)
UC_TX: TP18.1, U1.51 (PC10)
USB_D+: J5.A7 (D-), J5.B7 (D-), R4.1, TP2.1, U1.45 (PA12)
USB_D-: J5.A6 (D+), J5.B6 (D+), TP3.1, U1.44 (PA11)

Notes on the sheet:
I2C pullups
Debug LEDs
UC BUTTONS
Potentiometers
ADC inputs
JTAG debugging
MICROCONTROLLER
Battery
EMG ADC inputs
Just in case I2C
Haptic feedback motors
USB
Push button
4x M3 plated mounting holes in corners
Solder jumpers for HW variant coding
TODO: - Make a bill of materials (BOM) - Keep as much clearance between traces as possible/available - Add some graphics and logos on silkscreen - Add version somewhere also on siklscreen - Add JLC order number on PCB - Double-check all the footprint sizes and dimensions
Battery voltage sense divider: - max bat voltage ~12.6V - gives us ~2.2V on output
Motors
MOUNTING
CONNECTORS
PCB design parameters: - min trace width 0.2mm and spacing 0.2mm - via hole size/diameter: 0.3mm / 0.5mm
HW REV
For resetting/programming the board
YT: STM32 PCB Design - Complete Walkthrough - Phil's Lab #41
USB Type C connector
STM32 decoupling caps
USER INTERFACE
Buttons for RST and BOOT
STM32F103RET6
YT: Aesthetic PCB Design Tips - Phil's Lab #84
Finger position hall effect sensor
Just in case UART
EMG sensors
Direct USB device connection
JTAG

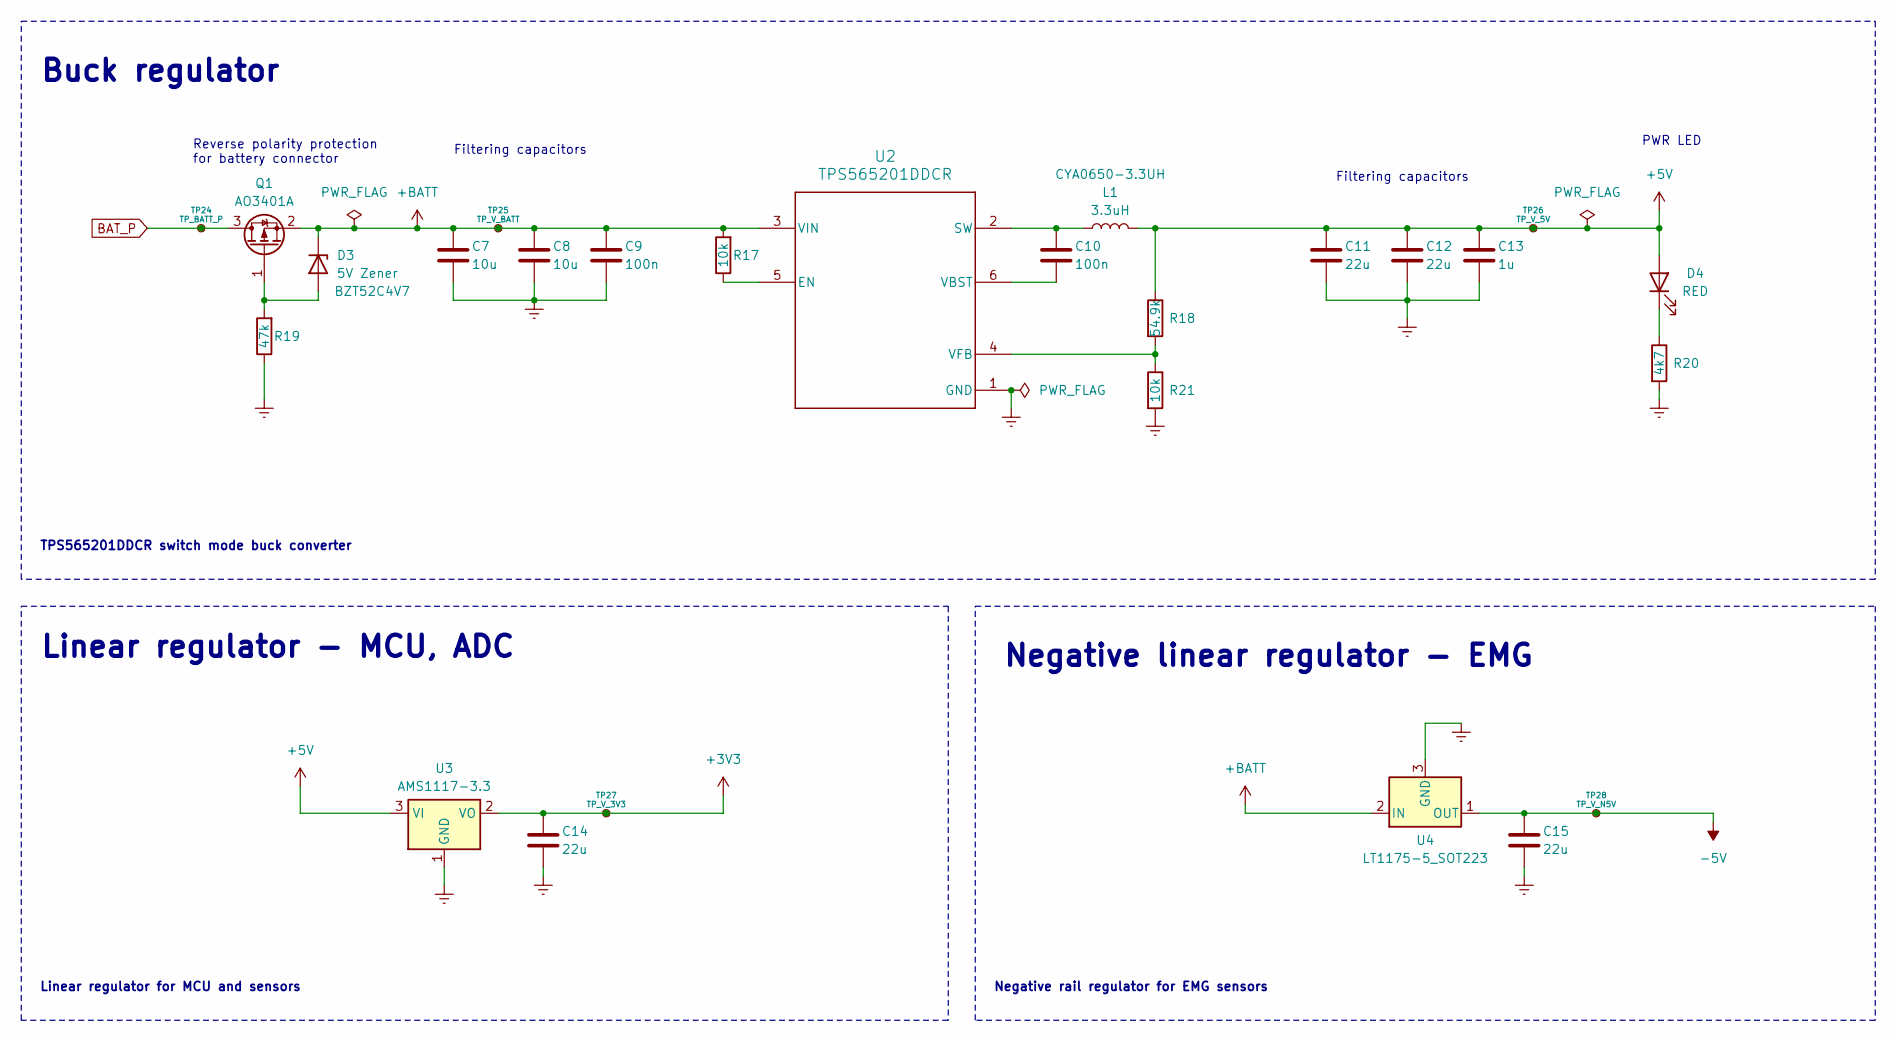
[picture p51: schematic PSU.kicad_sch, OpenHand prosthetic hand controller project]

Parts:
C7, C8: 10u; C_0805_2012Metric
C9, C10: 100n; C_0805_2012Metric
C11, C12, C14, C15: 22u; C_0805_2012Metric
C13: 1u; C_0805_2012Metric
D3: 5V Zener; D_SOD-123; Part Number BZT52C4V7
D4: RED; LED_1210_3225Metric
L1: 3.3uH; L_Bourns_SRP7028A_7.3x6.6mm; Part Number CYA0650-3.3UH
Q1: AO3401A; SOT-23
R17, R21: 10k; R_0805_2012Metric
R18: 54.9k; R_0805_2012Metric
R19: 47k; R_0805_2012Metric
R20: 4k7; R_0805_2012Metric
TP24: TP_BATT_P; TestPoint_Pad_D1.0mm
TP25: TP_V_BATT; TestPoint_Pad_D1.0mm
TP26: TP_V_5V; TestPoint_Pad_D1.0mm
TP27: TP_V_3V3; TestPoint_Pad_D1.0mm
TP28: TP_V_N5V; TestPoint_Pad_D1.0mm
U2: TPS565201DDCR; TPS565201DDCR_L
U3: AMS1117-3.3; SOT-223-3_TabPin2
U4: LT1175-5_SOT223; SOT-223-3_TabPin2

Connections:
+3V3: C14.1, TP27.1, U3.2 (VO); also elsewhere on the board
+5V: C11.1, C12.1, C13.1, D4.2 (A), L1.2, R18.1, TP26.1, U3.3 (VI); also elsewhere on the board
+BATT: C7.1, C8.1, C9.1, D3.1 (K), Q1.2 (S), R17.2, TP25.1, U2.3 (VIN), U4.2 (IN); also elsewhere on the board
-5V: C15.1, TP28.1, U4.1 (OUT); also elsewhere on the board
BAT_P: Q1.3 (D), TP24.1; also elsewhere on the board
Earth: C7.2, C8.2, C9.2, C11.2, C12.2, C13.2, C14.2, C15.2, R19.1, R20.2, R21.2, U2.1 (GND), U3.1 (GND), U4.3 (GND); also elsewhere on the board
unnamed: D3.2 (A), Q1.1 (G), R19.2
unnamed: D4.1 (K), R20.1
unnamed: R17.1, U2.5 (EN)
unnamed: C10.1, L1.1, U2.2 (SW)
unnamed: C10.2, U2.6 (VBST)
unnamed: R18.2, R21.1, U2.4 (VFB)

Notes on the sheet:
Linear regulator - MCU, ADC
Filtering capacitors
PWR LED
Negative linear regulator - EMG
Buck regulator
TPS565201DDCR switch mode buck converter
Negative rail regulator for EMG sensors
Linear regulator for MCU and sensors
Reverse polarity protection for battery connector

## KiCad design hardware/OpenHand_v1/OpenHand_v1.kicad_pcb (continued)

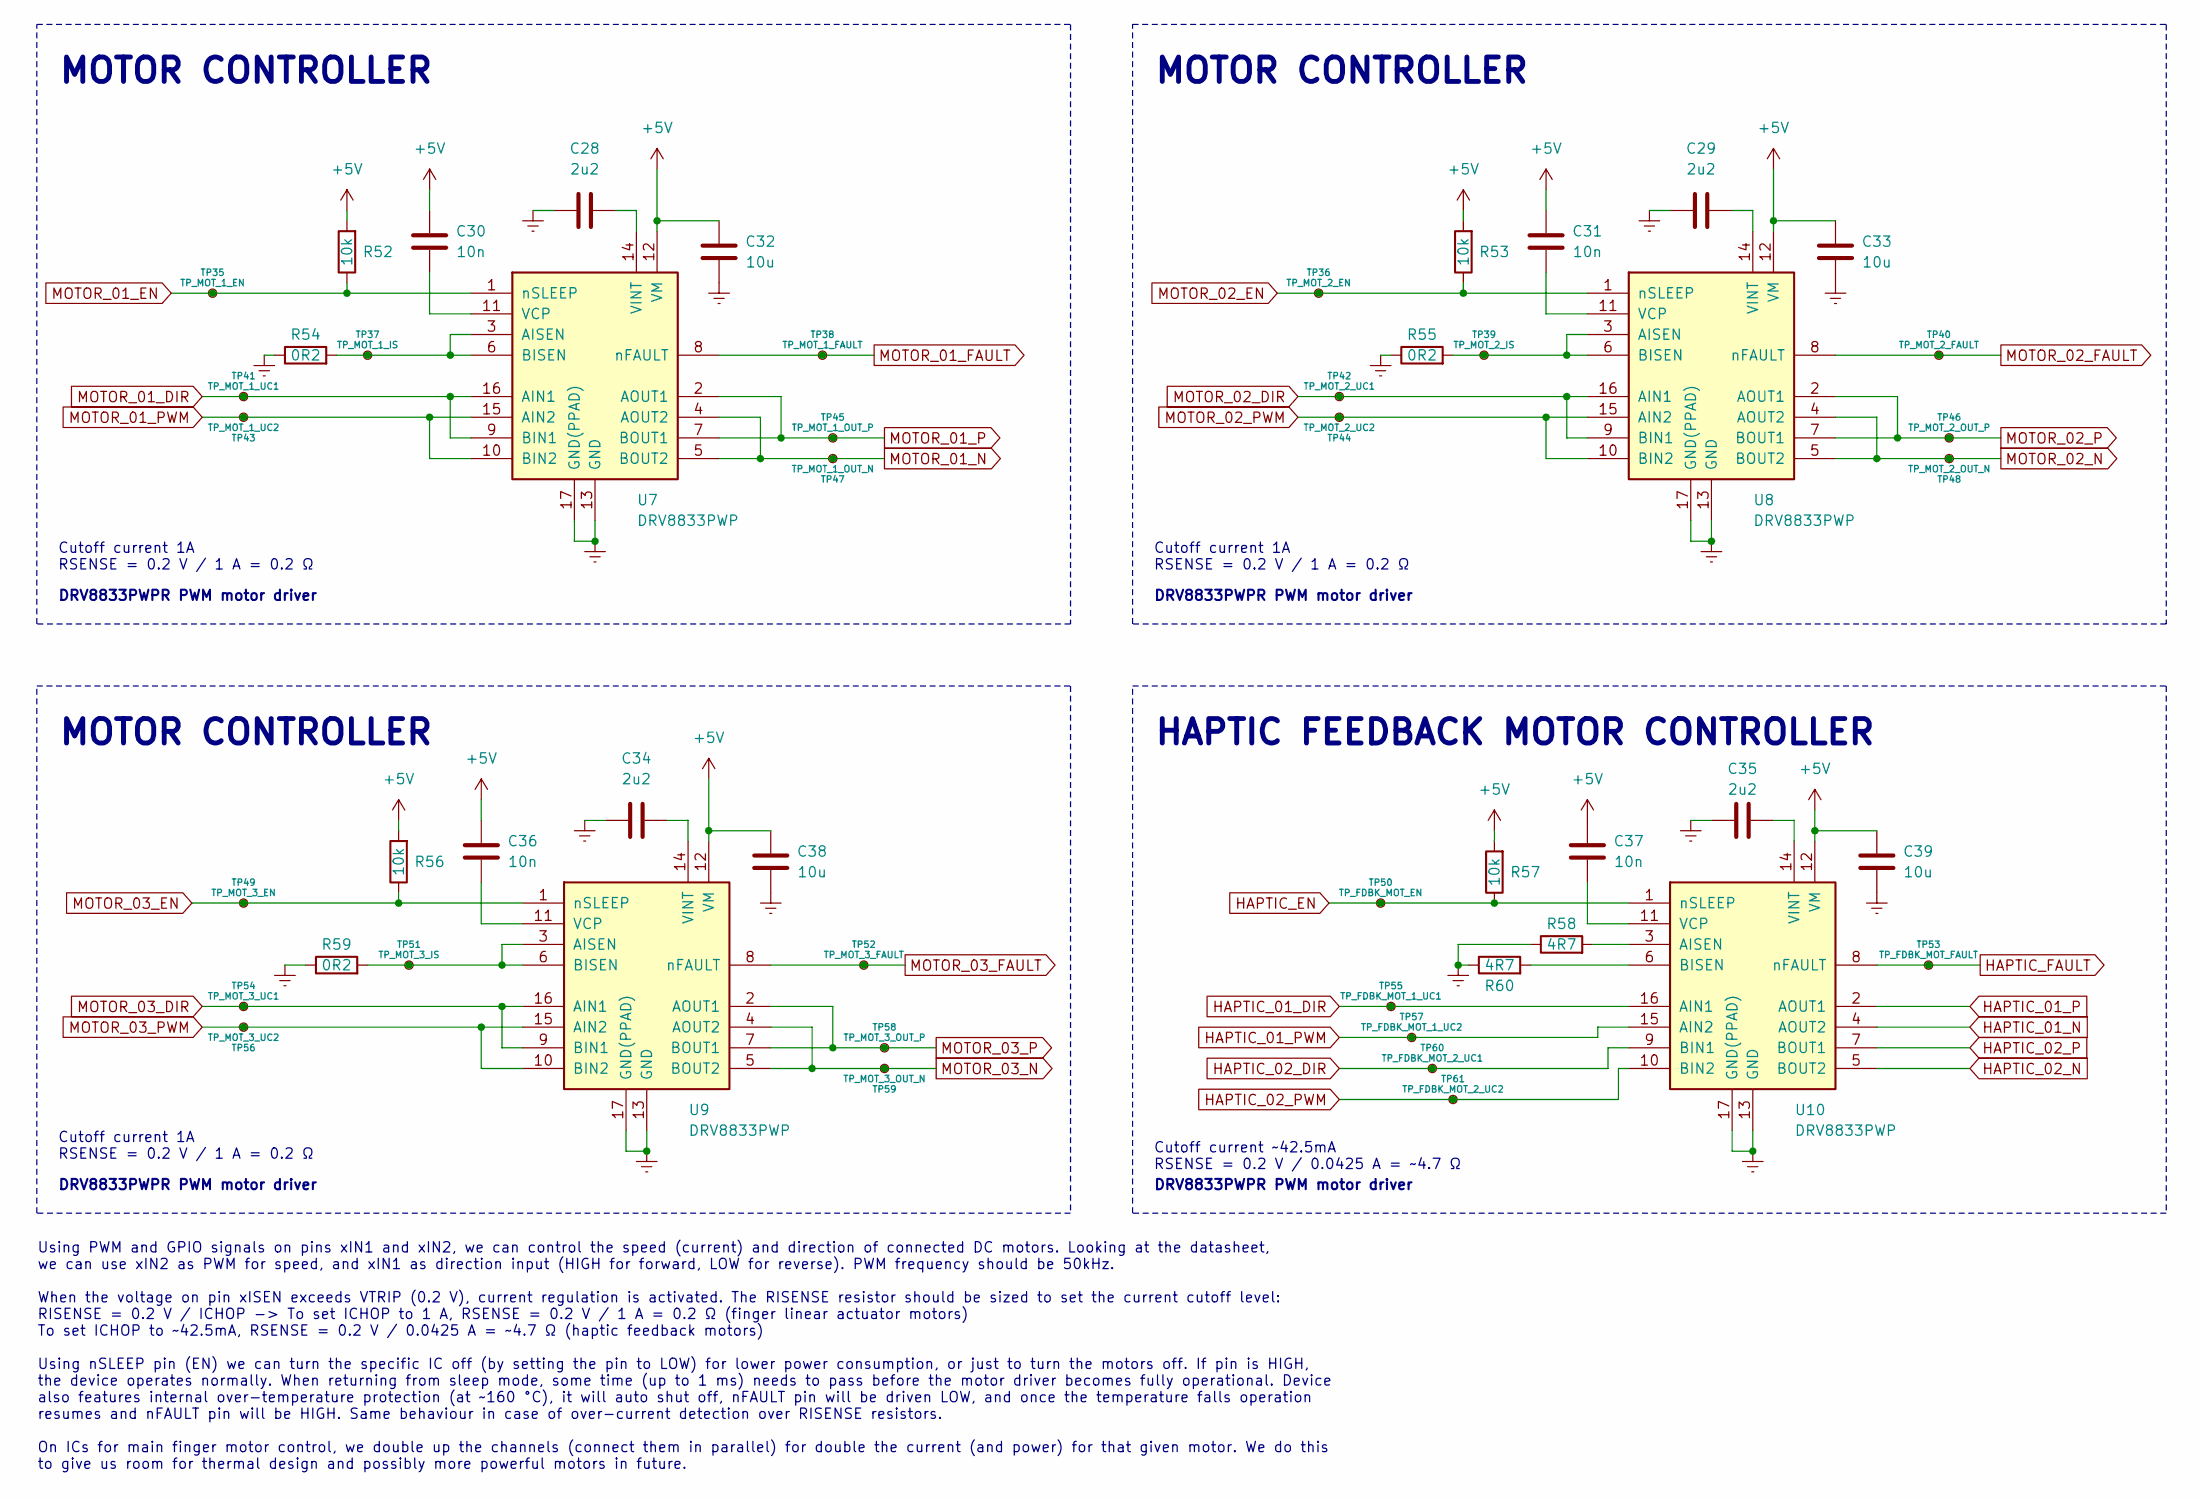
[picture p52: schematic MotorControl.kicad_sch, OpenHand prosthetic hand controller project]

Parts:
C28, C29, C34, C35: 2u2; C_0805_2012Metric
C30, C31, C36, C37: 10n; C_0805_2012Metric
C32, C33, C38, C39: 10u; C_0805_2012Metric
R52, R53, R56, R57: 10k; R_0805_2012Metric
R54, R55, R59: 0R2; R_1206_3216Metric
R58, R60: 4R7; R_1206_3216Metric
TP35: TP_MOT_1_EN; TestPoint_Pad_D1.0mm
TP36: TP_MOT_2_EN; TestPoint_Pad_D1.0mm
TP37: TP_MOT_1_IS; TestPoint_Pad_D1.0mm
TP38: TP_MOT_1_FAULT; TestPoint_Pad_D1.0mm
TP39: TP_MOT_2_IS; TestPoint_Pad_D1.0mm
TP40: TP_MOT_2_FAULT; TestPoint_Pad_D1.0mm
TP41: TP_MOT_1_UC1; TestPoint_Pad_D1.0mm
TP42: TP_MOT_2_UC1; TestPoint_Pad_D1.0mm
TP43: TP_MOT_1_UC2; TestPoint_Pad_D1.0mm
TP44: TP_MOT_2_UC2; TestPoint_Pad_D1.0mm
TP45: TP_MOT_1_OUT_P; TestPoint_Pad_D1.0mm
TP46: TP_MOT_2_OUT_P; TestPoint_Pad_D1.0mm
TP47: TP_MOT_1_OUT_N; TestPoint_Pad_D1.0mm
TP48: TP_MOT_2_OUT_N; TestPoint_Pad_D1.0mm
TP49: TP_MOT_3_EN; TestPoint_Pad_D1.0mm
TP50: TP_FDBK_MOT_EN; TestPoint_Pad_D1.0mm
TP51: TP_MOT_3_IS; TestPoint_Pad_D1.0mm
TP52: TP_MOT_3_FAULT; TestPoint_Pad_D1.0mm
TP53: TP_FDBK_MOT_FAULT; TestPoint_Pad_D1.0mm
TP54: TP_MOT_3_UC1; TestPoint_Pad_D1.0mm
TP55: TP_FDBK_MOT_1_UC1; TestPoint_Pad_D1.0mm
TP56: TP_MOT_3_UC2; TestPoint_Pad_D1.0mm
TP57: TP_FDBK_MOT_1_UC2; TestPoint_Pad_D1.0mm
TP58: TP_MOT_3_OUT_P; TestPoint_Pad_D1.0mm
TP59: TP_MOT_3_OUT_N; TestPoint_Pad_D1.0mm
TP60: TP_FDBK_MOT_2_UC1; TestPoint_Pad_D1.0mm
TP61: TP_FDBK_MOT_2_UC2; TestPoint_Pad_D1.0mm
U7, U8, U9, U10: DRV8833PWP; HTSSOP-16-1EP_4.4x5mm_P0.65mm_EP3.4x5mm_Mask2.46x2.31mm_The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

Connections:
+5V: C30.1, C31.1, C32.1, C33.1, C36.1, C37.1, C38.1, C39.1, R52.2, R53.2, R56.2, R57.2, U7.12 (VM), U8.12 (VM), U9.12 (VM), U10.12 (VM); also elsewhere on the board
Earth: C28.1, C29.1, C32.2, C33.2, C34.1, C35.1, C38.2, C39.2, R54.1, R55.1, R58.1, R59.1, R60.1, U7.13 (GND), U7.17 (GND(PPAD)), U8.13 (GND), U8.17 (GND(PPAD)), U9.13 (GND), U9.17 (GND(PPAD)), U10.13 (GND), U10.17 (GND(PPAD)); also elsewhere on the board
HAPTIC_01_DIR: TP55.1, U10.16 (AIN1); also elsewhere on the board
HAPTIC_01_N: U10.4 (AOUT2); also elsewhere on the board
HAPTIC_01_P: U10.2 (AOUT1); also elsewhere on the board
HAPTIC_01_PWM: TP57.1, U10.15 (AIN2); also elsewhere on the board
HAPTIC_02_DIR: TP60.1, U10.9 (BIN1); also elsewhere on the board
HAPTIC_02_N: U10.5 (BOUT2); also elsewhere on the board
HAPTIC_02_P: U10.7 (BOUT1); also elsewhere on the board
HAPTIC_02_PWM: TP61.1, U10.10 (BIN2); also elsewhere on the board
HAPTIC_EN: R57.1, TP50.1, U10.1 (nSLEEP); also elsewhere on the board
HAPTIC_FAULT: TP53.1, U10.8 (nFAULT); also elsewhere on the board
MOTOR_01_DIR: TP41.1, U7.9 (BIN1), U7.16 (AIN1); also elsewhere on the board
MOTOR_01_EN: R52.1, TP35.1, U7.1 (nSLEEP); also elsewhere on the board
MOTOR_01_FAULT: TP38.1, U7.8 (nFAULT); also elsewhere on the board
MOTOR_01_N: TP47.1, U7.4 (AOUT2), U7.5 (BOUT2); also elsewhere on the board
MOTOR_01_P: TP45.1, U7.2 (AOUT1), U7.7 (BOUT1); also elsewhere on the board
MOTOR_01_PWM: TP43.1, U7.10 (BIN2), U7.15 (AIN2); also elsewhere on the board
MOTOR_02_DIR: TP42.1, U8.9 (BIN1), U8.16 (AIN1); also elsewhere on the board
MOTOR_02_EN: R53.1, TP36.1, U8.1 (nSLEEP); also elsewhere on the board
MOTOR_02_FAULT: TP40.1, U8.8 (nFAULT); also elsewhere on the board
MOTOR_02_N: TP48.1, U8.4 (AOUT2), U8.5 (BOUT2); also elsewhere on the board
MOTOR_02_P: TP46.1, U8.2 (AOUT1), U8.7 (BOUT1); also elsewhere on the board
MOTOR_02_PWM: TP44.1, U8.10 (BIN2), U8.15 (AIN2); also elsewhere on the board
MOTOR_03_DIR: TP54.1, U9.9 (BIN1), U9.16 (AIN1); also elsewhere on the board
MOTOR_03_EN: R56.1, TP49.1, U9.1 (nSLEEP); also elsewhere on the board
MOTOR_03_FAULT: TP52.1, U9.8 (nFAULT); also elsewhere on the board
MOTOR_03_N: TP59.1, U9.4 (AOUT2), U9.5 (BOUT2); also elsewhere on the board
MOTOR_03_P: TP58.1, U9.2 (AOUT1), U9.7 (BOUT1); also elsewhere on the board
MOTOR_03_PWM: TP56.1, U9.10 (BIN2), U9.15 (AIN2); also elsewhere on the board
unnamed: R54.2, TP37.1, U7.3 (AISEN), U7.6 (BISEN)
unnamed: C30.2, U7.11 (VCP)
unnamed: C28.2, U7.14 (VINT)
unnamed: R55.2, TP39.1, U8.3 (AISEN), U8.6 (BISEN)
unnamed: C31.2, U8.11 (VCP)
unnamed: C29.2, U8.14 (VINT)
unnamed: R59.2, TP51.1, U9.3 (AISEN), U9.6 (BISEN)
unnamed: C36.2, U9.11 (VCP)
unnamed: C34.2, U9.14 (VINT)
unnamed: R58.2, U10.3 (AISEN)
unnamed: R60.2, U10.6 (BISEN)
unnamed: C37.2, U10.11 (VCP)
unnamed: C35.2, U10.14 (VINT)

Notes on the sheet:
Cutoff current 1A RSENSE = 0.2 V / 1 A = 0.2 Ω
MOTOR CONTROLLER
DRV8833PWPR PWM motor driver
HAPTIC FEEDBACK MOTOR CONTROLLER
Using PWM and GPIO signals on pins xIN1 and xIN2, we can control the speed (current) and direction of connected DC motors. Looking at the datasheet, we can use xIN2 as PWM for speed, and xIN1 as direction input (HIGH for forward, LOW for reverse). PWM frequency should be 50kHz. When the voltage on 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
Cutoff current ~42.5mA RSENSE = 0.2 V / 0.0425 A = ~4.7 Ω

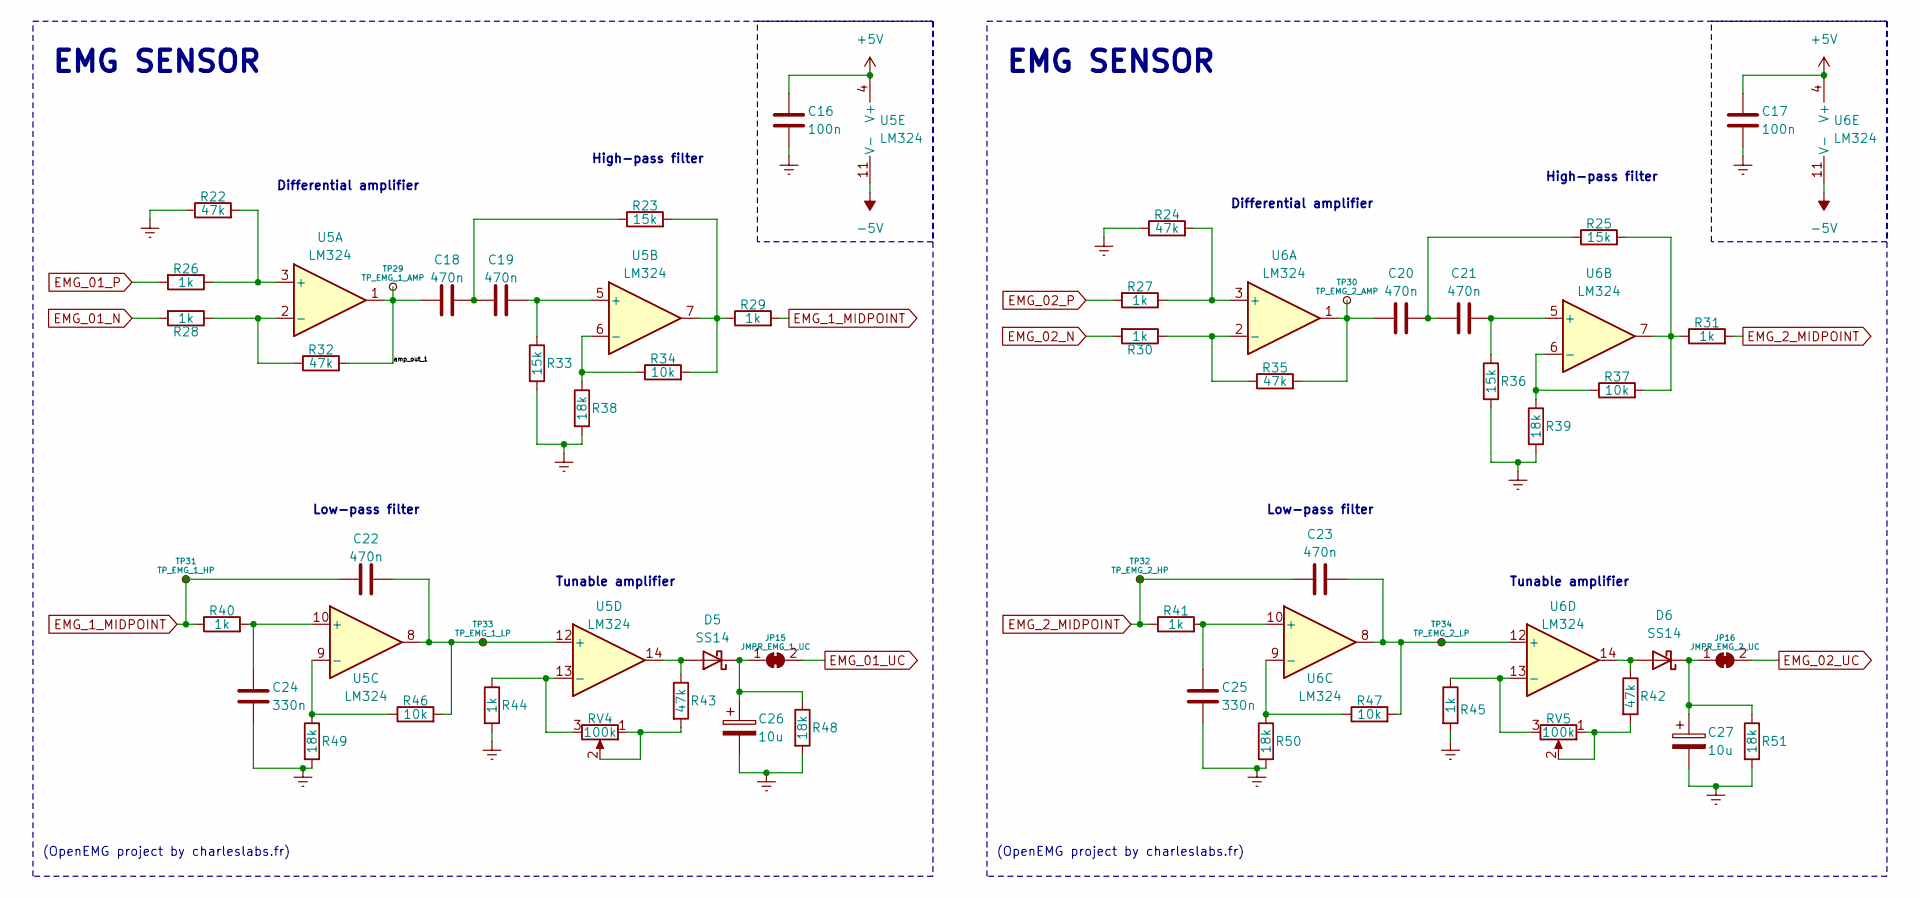
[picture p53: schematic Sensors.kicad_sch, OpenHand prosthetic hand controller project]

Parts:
C16, C17: 100n; C_0805_2012Metric
C18, C19, C20, C21, C22, C23: 470n; C_0805_2012Metric
C24, C25: 330n; C_0805_2012Metric
C26, C27: 10u; C_0805_2012Metric
D5, D6: SS14; D_SOD-123
JP15: JMPR_EMG_1_UC; SolderJumper-2_P1.3mm_Bridged_RoundedPad1.0x1.5mm
JP16: JMPR_EMG_2_UC; SolderJumper-2_P1.3mm_Bridged_RoundedPad1.0x1.5mm
R22, R24, R32, R35, R42, R43: 47k; R_0805_2012Metric
R23, R25, R33, R36: 15k; R_0805_2012Metric
R26, R27, R28, R29, R30, R31, R40, R41, R44, R45: 1k; R_0805_2012Metric
R34, R37, R46, R47: 10k; R_0805_2012Metric
R38, R39, R48, R49, R50, R51: 18k; R_0805_2012Metric
RV4, RV5: 100k; Potentiometer_Vishay_TS53YJ_Vertical
TP29: TP_EMG_1_AMP; TestPoint_Pad_D1.0mm
TP30: TP_EMG_2_AMP; TestPoint_Pad_D1.0mm
TP31: TP_EMG_1_HP; TestPoint_Pad_D1.0mm
TP32: TP_EMG_2_HP; TestPoint_Pad_D1.0mm
TP33: TP_EMG_1_LP; TestPoint_Pad_D1.0mm
TP34: TP_EMG_2_LP; TestPoint_Pad_D1.0mm
U5, U6: LM324; SO-14_5.3x10.2mm_P1.27mm

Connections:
+5V: C16.1, C17.1, U5.4 (V+), U6.4 (V+); also elsewhere on the board
-5V: U5.11 (V-), U6.11 (V-); also elsewhere on the board
/Sensors/amp_out_1: C18.1, R32.2, TP29.1, U5.1
EMG_1_MIDPOINT: C22.1, R29.2, R40.1, TP31.1
EMG_01_N: R28.2; also elsewhere on the board
EMG_01_P: R26.2; also elsewhere on the board
EMG_01_UC: JP15.2 (B); also elsewhere on the board
EMG_2_MIDPOINT: C23.1, R31.2, R41.1, TP32.1
EMG_02_N: R30.2; also elsewhere on the board
EMG_02_P: R27.2; also elsewhere on the board
EMG_02_UC: JP16.2 (B); also elsewhere on the board
Earth: C16.2, C17.2, C24.1, C25.1, C26.2, C27.2, R22.1, R24.1, R33.2, R36.2, R38.2, R39.2, R44.2, R45.2, R48.2, R49.2, R50.2, R51.2; also elsewhere on the board
unnamed: C18.2, C19.1, R23.1
unnamed: C20.1, R35.2, TP30.1, U6.1
unnamed: C20.2, C21.1, R25.1
unnamed: D5.2 (A), R43.1, U5.14
unnamed: C26.1, D5.1 (K), JP15.1 (A), R48.1
unnamed: D6.2 (A), R42.1, U6.14
unnamed: C27.1, D6.1 (K), JP16.1 (A), R51.1
unnamed: R23.2, R29.1, R34.2, U5.7
unnamed: R25.2, R31.1, R37.2, U6.7
unnamed: R42.2, RV5.1, RV5.2
unnamed: R43.2, RV4.1, RV4.2
unnamed: R22.2, R26.1, U5.3 (+)
unnamed: R28.1, R32.1, U5.2 (-)
unnamed: C19.2, R33.1, U5.5 (+)
unnamed: R34.1, R38.1, U5.6 (-)
unnamed: C24.2, R40.2, U5.10 (+)
unnamed: R46.1, R49.1, U5.9 (-)
unnamed: C22.2, R46.2, TP33.1, U5.8, U5.12 (+)
unnamed: R44.1, RV4.3, U5.13 (-)
unnamed: R24.2, R27.1, U6.3 (+)
unnamed: R30.1, R35.1, U6.2 (-)
unnamed: C21.2, R36.1, U6.5 (+)
unnamed: R37.1, R39.1, U6.6 (-)
unnamed: C25.2, R41.2, U6.10 (+)
unnamed: R47.1, R50.1, U6.9 (-)
unnamed: C23.2, R47.2, TP34.1, U6.8, U6.12 (+)
unnamed: R45.1, RV5.3, U6.13 (-)

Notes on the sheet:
EMG SENSOR
Low-pass filter
Differential amplifier
(OpenEMG project by charleslabs.fr)
High-pass filter
Tunable amplifier

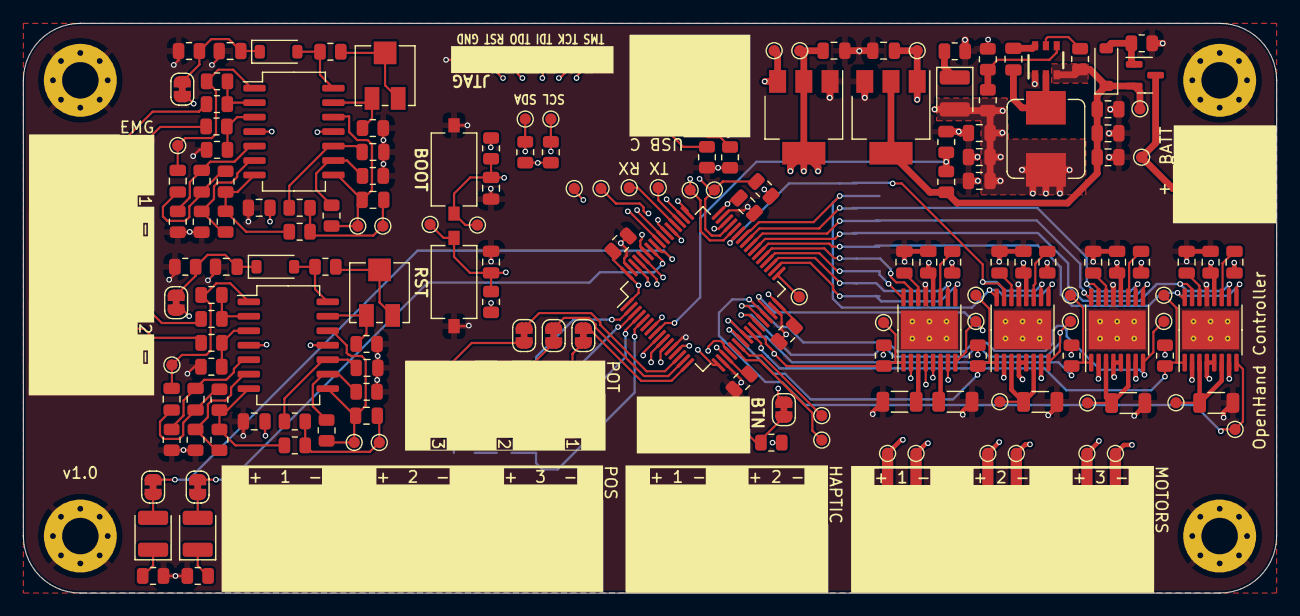
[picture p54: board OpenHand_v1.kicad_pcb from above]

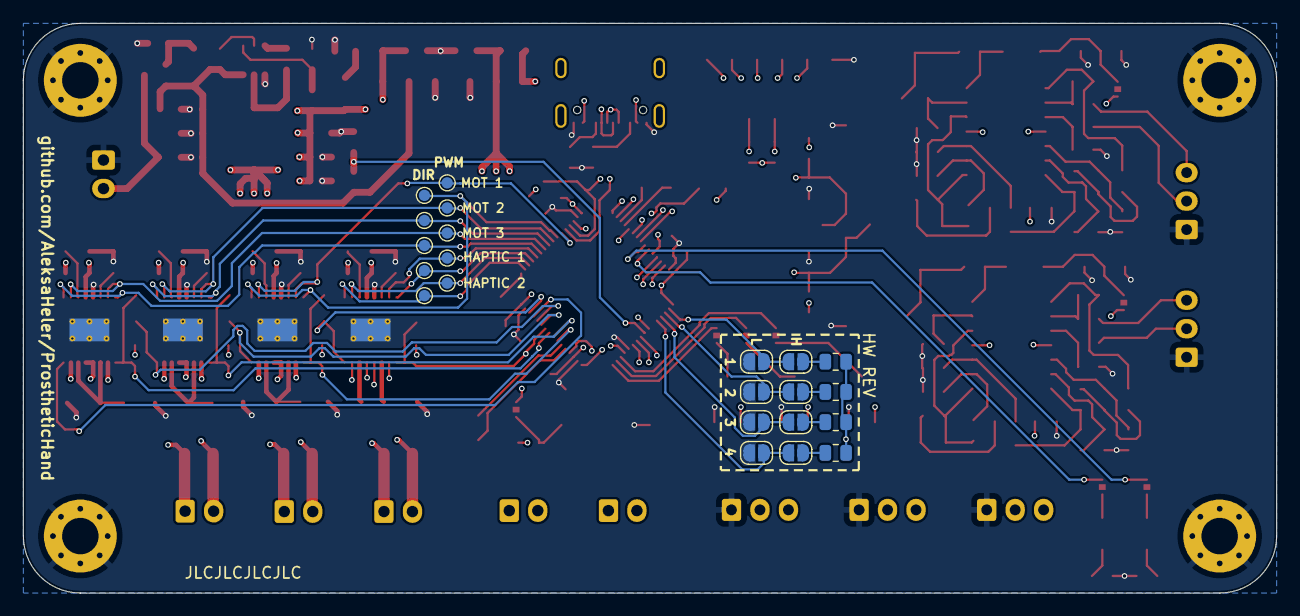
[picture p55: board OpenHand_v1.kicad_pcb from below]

Board: 4 copper layers, 110.0 x 50.0 mm, 214 parts (22 on the bottom side), 135 nets.

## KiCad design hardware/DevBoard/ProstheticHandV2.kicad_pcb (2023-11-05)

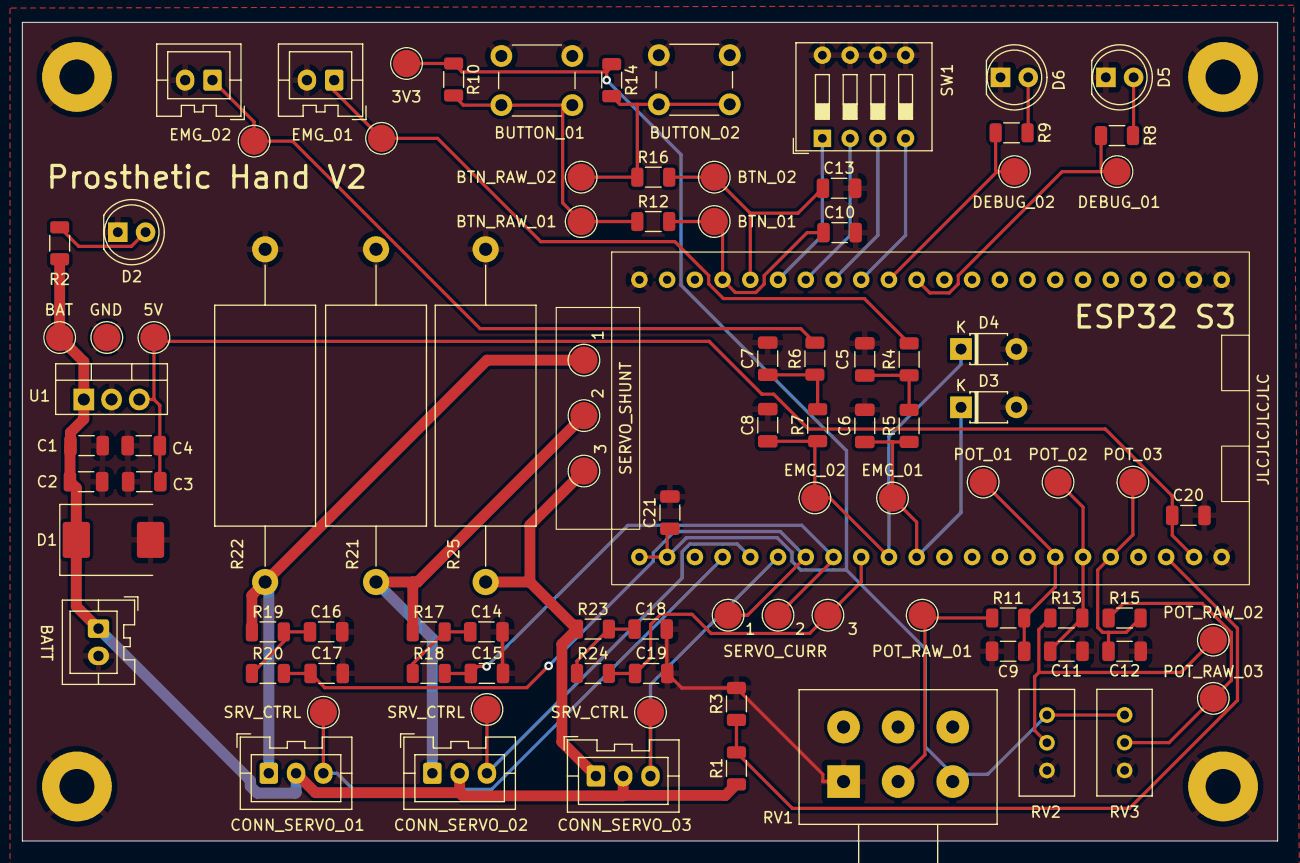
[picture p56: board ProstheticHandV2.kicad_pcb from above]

Board: 2 copper layers, 115.0 x 75.0 mm, 99 parts (0 on the bottom side), 42 nets.

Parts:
A1: ESP32S3_DevModule
C1, C3, C5, C6, C7, C8: 1uF; C_1206_3216Metric
C2, C4, C9, C10, C11, C12, C13, C20, C21: 0.1uF; C_1206_3216Metric
C14, C15, C16, C17, C18, C19: 100nF; C_1206_3216Metric
D1: SK36; D_SMC
D2: LED GREEN; LED_D5.0mm
D3, D4: 5v1; D_T-1_P5.08mm_Horizontal
D5: LED RED; LED_D5.0mm
D6: LED BLUE; LED_D5.0mm
H1, H2, H3, H4: MountingHole_Pad; MountingHole_3.2mm_M3_Pad
J1: BATT_CONNECTOR; JST_XA_B02B-XASK-1_1x02_P2.50mm_Vertical
J2: EMG_SENSOR_01; JST_XA_B02B-XASK-1_1x02_P2.50mm_Vertical
J3: EMG_SENSOR_02; JST_XA_B02B-XASK-1_1x02_P2.50mm_Vertical
J4: CONN_SERVO_02; JST_XA_B03B-XASK-1_1x03_P2.50mm_Vertical
J5: CONN_SERVO_01; JST_XA_B03B-XASK-1_1x03_P2.50mm_Vertical
J6: CONN_SERVO_03; JST_XA_B03B-XASK-1_1x03_P2.50mm_Vertical
R1: 4k7; R_1206_3216Metric
R2, R4, R5, R6, R7, R10, R11, R12, R13, R14, R15, R16: 10k; R_1206_3216Metric
R3, R17, R18, R19, R20, R23, R24: 1k; R_1206_3216Metric
R8, R9: 220; R_1206_3216Metric
R21, R22, R25: 0.1; R_Axial_DIN0922_L20.0mm_D9.0mm_P30.48mm_Horizontal
RV1: Pot. 5k; Potentiometer_Alps_RK163_Dual_Horizontal
RV2, RV3: Trim Pot. 10k; Potentiometer_Bourns_3296W_Vertical
SW1: DIP_SWITCH; SW_DIP_SPSTx04_Slide_9.78x12.34mm_W7.62mm_P2.54mm
SW2: BUTTON_01; SW_PUSH_6mm_H5mm
SW3: BUTTON_02; SW_PUSH_6mm_H5mm
TP1: TP_BATT; TestPoint_Pad_D2.5mm
TP2: TP_5V_REG; TestPoint_Pad_D2.5mm
TP3: TP_GND; TestPoint_Pad_D2.5mm
TP4: TP_EMG_01_IN; TestPoint_Pad_D2.5mm
TP5: TP_EMG_01_UC; TestPoint_Pad_D2.5mm
TP6: TP_EMG_02_IN; TestPoint_Pad_D2.5mm
TP7: TP_EMG_02_UC; TestPoint_Pad_D2.5mm
TP8: TP_DEBUG_01; TestPoint_Pad_D2.5mm
TP9: TP_DEBUG_02; TestPoint_Pad_D2.5mm
TP10: TP_3v3; TestPoint_Pad_D2.5mm
TP11: TP_POT_RAW_01; TestPoint_Pad_D2.5mm
TP12: TP_POT_01; TestPoint_Pad_D2.5mm
TP13: TP_BTN_RAW_01; TestPoint_Pad_D2.5mm
TP14: TP_BTN_01; TestPoint_Pad_D2.5mm
TP15: TP_POT_RAW_02; TestPoint_Pad_D2.5mm
TP16: TP_POT_02; TestPoint_Pad_D2.5mm
TP17: TP_POT_RAW_03; TestPoint_Pad_D2.5mm
TP18: TP_POT_03; TestPoint_Pad_D2.5mm
TP19: TP_BTN_RAW_02; TestPoint_Pad_D2.5mm
TP20: TP_BTN_02; TestPoint_Pad_D2.5mm
TP21: TP_SERVO_CONTROL_02; TestPoint_Pad_D2.5mm
TP22: TP_SERVO_CONTROL_01; TestPoint_Pad_D2.5mm
TP23: TP_SERVO_CURR_RAW_02; TestPoint_Pad_D2.5mm
TP24: TP_SERVO_CURR_02; TestPoint_Pad_D2.5mm
TP25: TP_SERVO_CURR_RAW_01; TestPoint_Pad_D2.5mm
TP26: TP_SERVO_CURR_01; TestPoint_Pad_D2.5mm
TP27: TP_SERVO_CONTROL_03; TestPoint_Pad_D2.5mm
TP28: TP_SERVO_CURR_RAW_03; TestPoint_Pad_D2.5mm
TP29: TP_SERVO_CURR_03; TestPoint_Pad_D2.5mm
U1: LM7805_TO220; TO-220-3_Vertical

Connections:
+3V3: A1.1 (3v3), A1.2 (3v3), C21.1, R10.1, R14.1, RV1.3, RV2.3, RV3.3, TP10.1
+5V: A1.21 (5v), C3.1, C4.1, C20.1, TP2.1, U1.3 (VO)
+BATT: C1.1, C2.1, D1.1 (K), J1.1, J4.2, J5.2, J6.2, R1.1, R2.1, TP1.1, U1.1 (VI)
BATT_SENSE: A1.20 (14), R1.2, R3.1
BUTTON_01: A1.41 (1), C10.1, R12.2, TP14.1
BUTTON_02: A1.40 (2), C13.1, R16.2, TP20.1
DEBUG_LED_01: A1.34 (37), R8.1, TP8.1
DEBUG_LED_02: A1.35 (38), R9.2, TP9.1
DIP_SWITCH_00: A1.39 (42), SW1.1
DIP_SWITCH_01: A1.38 (41), SW1.2
DIP_SWITCH_02: A1.37 (40), SW1.3
DIP_SWITCH_03: A1.36 (39), SW1.4
EMG_SENSOR_01: A1.11 (18), C6.1, D3.1 (K), R5.1, TP5.1
EMG_SENSOR_02: A1.10 (17), C8.1, D4.1 (K), R7.1, TP7.1
GND: A1.22 (GND), A1.23 (GND), A1.24 (GND), A1.44 (GND), C1.2, C2.2, C3.2, C4.2, C5.2, C6.2, C7.2, C8.2, C9.2, C10.2, C11.2, C12.2, C13.2, C14.2, C15.2, C16.2, C17.2, C18.2, C19.2, C20.2, C21.2, D1.2 (A), D2.1 (K), D3.2 (A), D4.2 (A), D5.1 (K), D6.1 (K), H1.1, H2.1, H3.1, H4.1, J1.2, J2.2, J3.2, R3.2, R21.2, R22.2, R25.2, RV1.1, RV2.1, RV3.1, SW1.5, SW1.6, SW1.7, SW1.8, SW2.1, SW3.1, TP3.1, U1.2 (GND)
unnamed: C5.1, R4.1, R5.2
unnamed: C7.1, R6.1, R7.2
unnamed: C14.1, R17.2, R18.1
unnamed: C16.1, R19.2, R20.1
unnamed: C18.1, R23.2, R24.1
unnamed: D2.2 (A), R2.2
unnamed: D5.2 (A), R8.2
unnamed: D6.2 (A), R9.1
unnamed: J2.1, R4.2, TP4.1
unnamed: J3.1, R6.2, TP6.1
unnamed: J4.1, R17.1, R21.1, TP23.1
unnamed: J5.1, R19.1, R22.1, TP25.1
unnamed: J6.1, R23.1, R25.1, TP28.1
unnamed: R10.2, R12.1, SW2.2, TP13.1
unnamed: R11.1, RV1.2, TP11.1
unnamed: R13.1, RV2.2, TP15.1
unnamed: R14.2, R16.1, SW3.2, TP19.1
unnamed: R15.1, RV3.2, TP17.1
POT_01: A1.16 (10), C9.1, R11.2, TP12.1
POT_02: A1.17 (11), C11.1, R13.2, TP16.1
POT_03: A1.18 (12), C12.1, R15.2, TP18.1
SERVO_CONTROL_01: A1.4, J5.3, TP22.1
SERVO_CONTROL_02: A1.5, J4.3, TP21.1
SERVO_CONTROL_03: A1.6, J6.3, TP27.1
SERVO_CURR_01: A1.7, C17.1, R20.2, TP26.1
SERVO_CURR_02: A1.8 (15), C15.1, R18.2, TP24.1
SERVO_CURR_03: A1.9 (16), C19.1, R24.2, TP29.1

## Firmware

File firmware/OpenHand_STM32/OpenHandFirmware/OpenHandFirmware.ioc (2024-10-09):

#MicroXplorer Configuration settings - do not modify
CAD.formats=
CAD.pinconfig=
CAD.provider=
FREERTOS.FootprintOK=true
FREERTOS.IPParameters=Tasks01,FootprintOK,configUSE_NEWLIB_REENTRANT
FREERTOS.Tasks01=hand_control,24,128,hand_control_function,Default,NULL,Dynamic,NULL,NULL;system_health,8,128,system_health_function,Default,NULL,Dynamic,NULL,NULL
FREERTOS.configUSE_NEWLIB_REENTRANT=1
File.Version=6
GPIO.groupedBy=Group By Peripherals
KeepUserPlacement=false
Mcu.CPN=STM32F103RBT6
Mcu.Family=STM32F1
Mcu.IP0=FREERTOS
Mcu.IP1=NVIC
Mcu.IP2=RCC
Mcu.IP3=SYS
Mcu.IP4=TIM1
Mcu.IP5=TIM3
Mcu.IPNb=6
Mcu.Name=STM32F103R(8-B)Tx
Mcu.Package=LQFP64
Mcu.Pin0=PD0-OSC_IN
Mcu.Pin1=PD1-OSC_OUT
Mcu.Pin10=PA10
Mcu.Pin11=PA13
Mcu.Pin12=PA14
Mcu.Pin13=PB5
Mcu.Pin14=PB6
Mcu.Pin15=PB7
Mcu.Pin16=VP_FREERTOS_VS_CMSIS_V2
Mcu.Pin17=VP_SYS_VS_tim4
Mcu.Pin2=PC5
Mcu.Pin3=PB1
Mcu.Pin4=PB10
Mcu.Pin5=PC7
Mcu.Pin6=PC8
Mcu.Pin7=PC9
Mcu.Pin8=PA8
Mcu.Pin9=PA9
Mcu.PinsNb=18
Mcu.ThirdPartyNb=0
Mcu.UserConstants=
Mcu.UserName=STM32F103RBTx
MxCube.Version=6.9.2
MxDb.Version=DB.6.0.92
NVIC.BusFault_IRQn=true\:0\:0\:false\:false\:true\:false\:false\:false\:false
NVIC.DebugMonitor_IRQn=true\:0\:0\:false\:false\:true\:false\:false\:false\:false
NVIC.ForceEnableDMAVector=true
NVIC.HardFault_IRQn=true\:0\:0\:false\:false\:true\:false\:false\:false\:false
NVIC.MemoryManagement_IRQn=true\:0\:0\:false\:false\:true\:false\:false\:false\:false
NVIC.NonMaskableInt_IRQn=true\:0\:0\:false\:false\:true\:false\:false\:false\:false
NVIC.PendSV_IRQn=true\:15\:0\:false\:false\:false\:true\:false\:false\:false
NVIC.PriorityGroup=NVIC_PRIORITYGROUP_4
NVIC.SVCall_IRQn=true\:0\:0\:false\:false\:false\:false\:false\:false\:false
NVIC.SavedPendsvIrqHandlerGenerated=true
NVIC.SavedSvcallIrqHandlerGenerated=true
NVIC.SavedSystickIrqHandlerGenerated=true
NVIC.SysTick_IRQn=true\:15\:0\:false\:false\:false\:true\:false\:true\:false
NVIC.TIM4_IRQn=true\:15\:0\:false\:false\:true\:false\:false\:true\:true
NVIC.TimeBase=TIM4_IRQn
NVIC.TimeBaseIP=TIM4
NVIC.UsageFault_IRQn=true\:0\:0\:false\:false\:true\:false\:false\:false\:false
PA10.GPIOParameters=GPIO_Label
PA10.GPIO_Label=MOTOR_03_PWM
PA10.Locked=true
PA10.Signal=S_TIM1_CH3
PA13.Mode=Serial_Wire
PA13.Signal=SYS_JTMS-SWDIO
PA14.Mode=Serial_Wire
PA14.Signal=SYS_JTCK-SWCLK
PA8.GPIOParameters=GPIO_Label
PA8.GPIO_Label=MOTOR_02_PWM
PA8.Locked=true
PA8.Signal=S_TIM1_CH1
PA9.GPIOParameters=GPIO_Label
PA9.GPIO_Label=MOTOR_03_DIR
PA9.Locked=true
PA9.Signal=GPIO_Output
PB1.GPIOParameters=GPIO_Label
PB1.GPIO_Label=MOTOR_02_EN
PB1.Locked=true
PB1.Signal=GPIO_Output
PB10.GPIOParameters=GPIO_Label
PB10.GPIO_Label=MOTOR_03_EN
PB10.Locked=true
PB10.Signal=GPIO_Output
PB5.GPIOParameters=GPIO_Label
PB5.GPIO_Label=LED_01
PB5.Locked=true
PB5.Signal=GPIO_Output
PB6.GPIOParameters=GPIO_Label
PB6.GPIO_Label=LED_02
PB6.Locked=true
PB6.Signal=GPIO_Output
PB7.GPIOParameters=GPIO_Label
PB7.GPIO_Label=BTN
PB7.Locked=true
PB7.Signal=GPIO_Input
PC5.GPIOParameters=GPIO_Label
PC5.GPIO_Label=MOTOR_01_EN
PC5.Locked=true
PC5.Signal=GPIO_Output
PC7.GPIOParameters=GPIO_Label
PC7.GPIO_Label=MOTOR_01_DIR
PC7.Locked=true
PC7.Signal=GPIO_Output
PC8.GPIOParameters=GPIO_Label
PC8.GPIO_Label=MOTOR_01_PWM
PC8.Locked=true
PC8.Signal=S_TIM3_CH3
PC9.GPIOParameters=GPIO_Label
PC9.GPIO_Label=MOTOR_02_DIR
PC9.Locked=true
PC9.Signal=GPIO_Output
PD0-OSC_IN.Mode=HSE-External-Oscillator
PD0-OSC_IN.Signal=RCC_OSC_IN
PD1-OSC_OUT.Mode=HSE-External-Oscillator
PD1-OSC_OUT.Signal=RCC_OSC_OUT
PinOutPanel.RotationAngle=0
ProjectManager.AskForMigrate=true
ProjectManager.BackupPrevious=false
ProjectManager.CompilerOptimize=6
ProjectManager.ComputerToolchain=false
ProjectManager.CoupleFile=false
ProjectManager.CustomerFirmwarePackage=
ProjectManager.DefaultFWLocation=true
ProjectManager.DeletePrevious=true
ProjectManager.DeviceId=STM32F103RBTx
ProjectManager.FirmwarePackage=STM32Cube FW_F1 V1.8.5
ProjectManager.FreePins=false
ProjectManager.HalAssertFull=false
ProjectManager.HeapSize=0x200
ProjectManager.KeepUserCode=true
ProjectManager.LastFirmware=false
ProjectManager.LibraryCopy=1
ProjectManager.MainLocation=Core/Src
ProjectManager.NoMain=false
ProjectManager.PreviousToolchain=
ProjectManager.ProjectBuild=false
ProjectManager.ProjectFileName=OpenHandFirmware.ioc
ProjectManager.ProjectName=OpenHandFirmware
ProjectManager.ProjectStructure=
ProjectManager.RegisterCallBack=
ProjectManager.StackSize=0x400
ProjectManager.TargetToolchain=STM32CubeIDE
ProjectManager.ToolChainLocation=
ProjectManager.UAScriptAfterPath=
ProjectManager.UAScriptBeforePath=
ProjectManager.UnderRoot=true
ProjectManager.functionlistsort=1-SystemClock_Config-RCC-false-HAL-false,2-MX_GPIO_Init-GPIO-false-HAL-true,3-MX_TIM1_Init-TIM1-false-HAL-true,4-MX_TIM3_Init-TIM3-false-HAL-true
RCC.ADCFreqValue=12000000
RCC.ADCPresc=RCC_ADCPCLK2_DIV6
RCC.AHBFreq_Value=72000000
RCC.APB1CLKDivider=RCC_HCLK_DIV2
RCC.APB1Freq_Value=36000000
RCC.APB1TimFreq_Value=72000000
RCC.APB2Freq_Value=72000000
RCC.APB2TimFreq_Value=72000000
RCC.FCLKCortexFreq_Value=72000000
RCC.FamilyName=M
RCC.HCLKFreq_Value=72000000
RCC.HSEDivPLL=RCC_HSE_PREDIV_DIV2
RCC.HSE_VALUE=16000000
RCC.IPParameters=ADCFreqValue,ADCPresc,AHBFreq_Value,APB1CLKDivider,APB1Freq_Value,APB1TimFreq_Value,APB2Freq_Value,APB2TimFreq_Value,FCLKCortexFreq_Value,FamilyName,HCLKFreq_Value,HSEDivPLL,HSE_VALUE,MCOFreq_Value,PLLCLKFreq_Value,PLLMCOFreq_Value,PLLMUL,PLLSourceVirtual,SYSCLKFreq_VALUE,SYSCLKSource,TimSysFreq_Value,USBFreq_Value,USBPrescaler,VCOOutput2Freq_Value
RCC.MCOFreq_Value=72000000
RCC.PLLCLKFreq_Value=72000000
RCC.PLLMCOFreq_Value=36000000
RCC.PLLMUL=RCC_PLL_MUL9
RCC.PLLSourceVirtual=RCC_PLLSOURCE_HSE
RCC.SYSCLKFreq_VALUE=72000000
RCC.SYSCLKSource=RCC_SYSCLKSOURCE_PLLCLK
RCC.TimSysFreq_Value=72000000
RCC.USBFreq_Value=48000000
RCC.USBPrescaler=RCC_USBCLKSOURCE_PLL_DIV1_5
RCC.VCOOutput2Freq_Value=8000000
SH.S_TIM1_CH1.0=TIM1_CH1,PWM Generation1 CH1
SH.S_TIM1_CH1.ConfNb=1
SH.S_TIM1_CH3.0=TIM1_CH3,PWM Generation3 CH3
SH.S_TIM1_CH3.ConfNb=1
SH.S_TIM3_CH3.0=TIM3_CH3,PWM Generation3 CH3
SH.S_TIM3_CH3.ConfNb=1
TIM1.AutoReloadPreload=TIM_AUTORELOAD_PRELOAD_DISABLE
TIM1.Channel-PWM\ Generation1\ CH1=TIM_CHANNEL_1
TIM1.Channel-PWM\ Generation3\ CH3=TIM_CHANNEL_3
TIM1.IPParameters=Channel-PWM Generation3 CH3,Channel-PWM Generation1 CH1,Period,Prescaler,AutoReloadPreload
TIM1.Period=20-1
TIM1.Prescaler=72
TIM3.AutoReloadPreload=TIM_AUTORELOAD_PRELOAD_DISABLE
TIM3.Channel-PWM\ Generation3\ CH3=TIM_CHANNEL_3
TIM3.IPParameters=Channel-PWM Generation3 CH3,Prescaler,Period,AutoReloadPreload
TIM3.Period=20-1
TIM3.Prescaler=72
VP_FREERTOS_VS_CMSIS_V2.Mode=CMSIS_V2
VP_FREERTOS_VS_CMSIS_V2.Signal=FREERTOS_VS_CMSIS_V2
VP_SYS_VS_tim4.Mode=TIM4
VP_SYS_VS_tim4.Signal=SYS_VS_tim4
board=custom
rtos.0.ip=FREERTOS
isbadioc=false

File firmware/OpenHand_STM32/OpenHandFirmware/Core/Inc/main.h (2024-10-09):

/* USER CODE BEGIN Header */
/**
  ******************************************************************************
  * @file           : main.h
  * @brief          : Header for main.c file.
  *                   This file contains the common defines of the application.
  ******************************************************************************
  * @attention
  *
  * Copyright (c) 2024 STMicroelectronics.
  * All rights reserved.
  *
  * This software is licensed under terms that can be found in the LICENSE file
  * in the root directory of this software component.
  * If no LICENSE file comes with this software, it is provided AS-IS.
  *
  ******************************************************************************
  */
/* USER CODE END Header */

/* Define to prevent recursive inclusion -------------------------------------*/
#ifndef __MAIN_H
#define __MAIN_H

#ifdef __cplusplus
extern "C" {
#endif

/* Includes ------------------------------------------------------------------*/
#include "stm32f1xx_hal.h"

/* Private includes ----------------------------------------------------------*/
/* USER CODE BEGIN Includes */

/* USER CODE END Includes */

/* Exported types ------------------------------------------------------------*/
/* USER CODE BEGIN ET */

/* USER CODE END ET */

/* Exported constants --------------------------------------------------------*/
/* USER CODE BEGIN EC */

/* USER CODE END EC */

/* Exported macro ------------------------------------------------------------*/
/* USER CODE BEGIN EM */

/* USER CODE END EM */

void HAL_TIM_MspPostInit(TIM_HandleTypeDef *htim);

/* Exported functions prototypes ---------------------------------------------*/
void Error_Handler(void);

/* USER CODE BEGIN EFP */

/* USER CODE END EFP */

/* Private defines -----------------------------------------------------------*/
#define MOTOR_01_EN_Pin GPIO_PIN_5
#define MOTOR_01_EN_GPIO_Port GPIOC
#define MOTOR_02_EN_Pin GPIO_PIN_1
#define MOTOR_02_EN_GPIO_Port GPIOB
#define MOTOR_03_EN_Pin GPIO_PIN_10
#define MOTOR_03_EN_GPIO_Port GPIOB
#define MOTOR_01_DIR_Pin GPIO_PIN_7
#define MOTOR_01_DIR_GPIO_Port GPIOC
#define MOTOR_01_PWM_Pin GPIO_PIN_8
#define MOTOR_01_PWM_GPIO_Port GPIOC
#define MOTOR_02_DIR_Pin GPIO_PIN_9
#define MOTOR_02_DIR_GPIO_Port GPIOC
#define MOTOR_02_PWM_Pin GPIO_PIN_8
#define MOTOR_02_PWM_GPIO_Port GPIOA
#define MOTOR_03_DIR_Pin GPIO_PIN_9
#define MOTOR_03_DIR_GPIO_Port GPIOA
#define MOTOR_03_PWM_Pin GPIO_PIN_10
#define MOTOR_03_PWM_GPIO_Port GPIOA
#define LED_01_Pin GPIO_PIN_5
#define LED_01_GPIO_Port GPIOB
#define LED_02_Pin GPIO_PIN_6
#define LED_02_GPIO_Port GPIOB
#define BTN_Pin GPIO_PIN_7
#define BTN_GPIO_Port GPIOB

/* USER CODE BEGIN Private defines */

/* USER CODE END Private defines */

#ifdef __cplusplus
}
#endif

#endif /* __MAIN_H */

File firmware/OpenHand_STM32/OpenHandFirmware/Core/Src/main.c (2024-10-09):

/* USER CODE BEGIN Header */
/**
  ******************************************************************************
  * @file           : main.c
  * @brief          : Main program body
  ******************************************************************************
  * @attention
  *
  * Copyright (c) 2024 STMicroelectronics.
  * All rights reserved.
  *
  * This software is licensed under terms that can be found in the LICENSE file
  * in the root directory of this software component.
  * If no LICENSE file comes with this software, it is provided AS-IS.
  *
  ******************************************************************************
  */
/* USER CODE END Header */
/* Includes ------------------------------------------------------------------*/
#include "main.h"
#include "cmsis_os.h"

/* Private includes ----------------------------------------------------------*/
/* USER CODE BEGIN Includes */
#include "led/led_e.h"
#include "btn/btn_e.h"
// #include "motor_e.h"...
/* USER CODE END Includes */

/* Private typedef -----------------------------------------------------------*/
/* USER CODE BEGIN PTD */
/* USER CODE END PTD */

/* Private define ------------------------------------------------------------*/
/* USER CODE BEGIN PD */
/* USER CODE END PD */

/* Private macro -------------------------------------------------------------*/
/* USER CODE BEGIN PM */
/* USER CODE END PM */

/* Private variables ---------------------------------------------------------*/
TIM_HandleTypeDef htim1;
TIM_HandleTypeDef htim3;

/* Definitions for hand_control */
osThreadId_t hand_controlHandle;
const osThreadAttr_t hand_control_attributes = {
  .name = "hand_control",
  .stack_size = 128 * 4,
  .priority = (osPriority_t) osPriorityNormal,
};
/* Definitions for system_health */
osThreadId_t system_healthHandle;
const osThreadAttr_t system_health_attributes = {
  .name = "system_health",
  .stack_size = 128 * 4,
  .priority = (osPriority_t) osPriorityLow,
};
/* USER CODE BEGIN PV */

// ADC stuff
volatile uint16_t adcResultsDMA[64][8]; // 64 measurements per channel, 8 channels
const int adcChannelCount = sizeof(adcResultsDMA) / sizeof(uint16_t);
volatile int adcConversionComplete = 0; // Set by callback

// Mode handling stuff
uint32_t my_mode = 0; // 0 for button activation, 1 for EMG sensor activation

// Our ADC inputs
uint32_t my_pot_1 = 0;
uint32_t my_pot_2 = 0;
uint32_t my_emg_1 = 0;
uint32_t my_emg_2 = 0;
uint32_t my_batt = 0;
uint32_t my_hall_1 = 0;
uint32_t my_hall_2 = 0;
uint32_t my_hall_3 = 0;

double my_batt_volt = 0;
uint32_t my_emg_1_max = 0;

// Finger hall sensor calibration output:
uint16_t my_calibration[] = {
  2024, 1889,
  2026, 1888,
  2024, 1890,
  2024, 1887,
  2023, 1883,
  2022, 1878,
  2021, 1875,
  2019, 1868,
  2019, 1863,
  2019, 1857,
  2017, 1850,
  2016, 1840,
  2015, 1830,
  2014, 1818,
  2012, 1806,
  2010, 1794,
  2008, 1783,
  2007, 1768,
  2006, 1755,
  2005, 1739,
  2001, 1724,
  2000, 1708,
  1996, 1690,
  1995, 1675,
  1994, 1655,
  1992, 1635,
  1989, 1614,
  1987, 1592,
  1984, 1574,
  1982, 1550,
  1978, 1525,
  1975, 1502,
  1974, 1479,
  1971, 1453,
  1968, 1429,
  1966, 1407,
  1962, 1379,
  1959, 1354,
  1955, 1328,
  1952, 1307,
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
};

/* USER CODE END PV */

/* Private function prototypes -----------------------------------------------*/
void SystemClock_Config(void);
static void MX_GPIO_Init(void);
static void MX_TIM1_Init(void);
static void MX_TIM3_Init(void);
void hand_control_function(void *argument);
void system_health_function(void *argument);

/* USER CODE BEGIN PFP */
void main_f_Init_v(void);
/* USER CODE END PFP */

/* Private user code ---------------------------------------------------------*/
/* USER CODE BEGIN 0 */

/**
 *  @todo Description
 *  @note Called once during boot
 */
void main_f_Init_v(void)
{
  /* Start all PWM channels */
  HAL_TIM_PWM_Start(&htim3, TIM_CHANNEL_3);  /* Motor 1 */
  HAL_TIM_PWM_Start(&htim1, TIM_CHANNEL_1);  /* Motor 2 */
  HAL_TIM_PWM_Start(&htim1, TIM_CHANNEL_3);  /* Motor 3 */
  //HAL_TIM_PWM_Start(&htim1, TIM_CHANNEL_2);
  //HAL_TIM_PWM_Start(&htim3, TIM_CHANNEL_1);

  // Read user button, if it's high, go to EMG mode
//  if (HAL_GPIO_ReadPin(GPIOB, GPIO_PIN_7) == GPIO_PIN_RESET)
//  {
//    my_mode = 1;
//  }
//  else
//  {
//    my_mode = 0;
//  }
}

/* USER CODE END 0 */
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

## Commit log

2022-05-04 Initial proof of concept tests with AD8232 heart beat sensor
    Good results
2022-05-06 Add Exponentially Weighted Moving Average Filter
2022-05-07 Removed EWMA filter and added highpass filter, works good
    See image of bicep activation with filter
2023-07-12 Add test finger joint
    [TestFingerJoint.3mf, TestFingerJoint.f3d]
2023-07-18 Add another test finger, and 2 research papers on joints
    [Finger 4 v4.f3d]
2023-08-26 Add basic code structure
    Add basic code structure and example of controlling servo with pot
    [ESP32_Pins.xlsx]
2023-08-29 Update file structures
    [Finger 4 v4.f3d, TestFingerJoint.3mf, TestFingerJoint.f3d]
2023-08-29 Update file structure, add HW project
    [DevelopmentBoard.kicad_pcb, DevelopmentBoard.kicad_sch]
2023-08-29 Add KiCAD HW design project
    [DevelopmentBoard.kicad_sch]
2023-08-30 Update development board hardware schematic
    [DevelopmentBoard.kicad_sch]
2023-08-31 Add ESP32 footprint to KiCAD
2023-09-01 Add PCB design for the HW test
    [DevelopmentBoard.kicad_pcb, DevelopmentBoard.kicad_sch]
2023-09-03 Prepare first dev board PCB to be homemade
    [DevelopmentBoard-B_Cu.gbl, DevelopmentBoard-B_Mask.gbs, DevelopmentBoard-B_Paste.gbp, DevelopmentBoard-B_Silkscreen.gbo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]
2023-09-03 Update ESP32 footprint
    [DevelopmentBoard-B_Cu.gbl, DevelopmentBoard-Edge_Cuts.gm1, DevelopmentBoard-F_Cu.gtl, DevelopmentBoard-F_Mask.gts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]
2023-09-03 Change framework from Arduino to ESP IDF
2023-09-06 Add new project for new PCB and document hardware folder
    [ProstheticHandV1.kicad_pcb, ProstheticHandV1.kicad_sch]
2023-09-06 Update docs for new PCB design
    [ESP32_Pins.xlsx]
2023-09-20 Migrate srv module to ESP IDF framework
2023-09-21 Started working on first real PCB
    [ProstheticHandV1.kicad_sch]
2023-09-21 Main migrated to ESP IDF framework
    Not yet tested on the hardware
2023-09-22 Main migrated to ESP IDF framework
    Not tested on the hardware yet
2023-09-23 Update code to somewhat work on ESP32, still WIP
2023-09-23 Updated HW readme with ideas for ESP32 S3
2023-09-23 KiCAD: Create symbol and footprint for ESP32 S3
    [ProstheticHandV1.kicad_sch]
2023-09-25 Started PCB design for hand V1
    [ProstheticHandV1.kicad_pcb, ProstheticHandV1.kicad_sch]
2023-09-25 Done hand PCB v1
    [ProstheticHandV1.kicad_pcb, ProstheticHandV1.kicad_sch]
2023-09-27 Add sensor driver module
2023-10-01 Add sensor module functionality
2023-10-01 Tweak sensor channel configuration
    Changed pin to GPIO 4 and lowered the ADC attenuation
2023-10-03 Change servo freq config
2023-10-03 Update schematic: jtag fix
    [ProstheticHandV1.kicad_pcb, ProstheticHandV1.kicad_sch]
2023-10-03 Made it work with ESP32 S3
2023-10-08 Update PCB for hand, completely new design
    [ProstheticHandV1.kicad_pcb, ProstheticHandV1.kicad_sch]
2023-10-08 Update code in main branch a bit
    [ProstheticHandV1.kicad_pcb, ProstheticHandV1.kicad_sch]
2023-10-09 Update button driver and schematic names
    [ProstheticHandV1.kicad_pcb, ProstheticHandV1.kicad_sch]
2023-10-09 remove processor type since we only use ESP32 S3
2023-10-09 Update pot & servo a bit
2023-10-11 Update duty cycle calculation to only be in servo working range and take min/max angle into account
2023-10-12 Update SERVO_MAX_ANGLE
2023-10-12 Create DIP Switch module
    Pin configuration and initialisation done
2023-10-12 Add signal source selection
    Not connected with the main program yet, can only read pin status and store it for now
2023-10-14 Update a lot of stuff in the code, tested with EMG sensor and servo, working!!!
2023-10-15 Add battery voltage sensing
2023-10-15 Add Fusion 360 hand model V1
    [ProstheticHand.3mf, ProstheticHand.f3d]
2023-10-17 Add REV02 - servo activation by button
2023-10-17 Add REV03 - control servo by sensor (threshold applied)
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2023-10-23 Started work on first PCB to be produced in china
    [BOM.xlsx, ProstheticHandV2.kicad_pcb, ProstheticHandV2.kicad_sch, untitled.kicad_sch]
2023-10-26 Update work on schematic
    [ProstheticHandV2.kicad_sch, ProstheticHandV2_Sheet2.kicad_sch, ProstheticHandV2_Sheet3.kicad_sch, untitled.kicad_sch]
2023-10-26 Started working on PCB
    [BOM.xlsx, ProstheticHandV2.kicad_pcb, ProstheticHandV2.kicad_sch, ProstheticHandV2_Sheet2.kicad_sch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]
2023-10-27 Finalize PCB design for china
    [ProstheticHandV2.kicad_pcb, ProstheticHandV2.kicad_sch, ProstheticHandV2_Sheet2.kicad_sch, ProstheticHandV2_Sheet3.kicad_sch]
2023-10-29 Update PCB & generate Gerber files
    [ProstheticHandV2-B_Cu.gbr, ProstheticHandV2-B_Mask.gbr, ProstheticHandV2-B_Paste.gbr, ProstheticHandV2-B_Silkscreen.gbr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]
2023-11-05 Update PCB, sent to JLCPCB
    [ProstheticHandV2-B_Cu.gbr, ProstheticHandV2-B_Mask.gbr, ProstheticHandV2-B_Paste.gbr, ProstheticHandV2-B_Silkscreen.gbr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]
2023-11-17 Update/cleanup hardware folder, add documentation and testing info
    [DevelopmentBoard-B_Cu.gbl, DevelopmentBoard-B_Mask.gbs, DevelopmentBoard-B_Paste.gbp, DevelopmentBoard-B_Silkscreen.gbo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]
2023-11-17 Update POC info and main readme file a bit
    [ESP32_Pins.xlsx, Finger 4 v4.f3d, ProstheticHand.3mf, ProstheticHand.f3d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]
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2023-12-03 Update sensor driver - fixed error
    For loop was incrementing i instead of j
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2024-01-24 Start new hardware design
    [Control.kicad_sch, OpenHand.kicad_pcb, OpenHand.kicad_sch, PSU.kicad_sch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]
2024-01-27 Minor comment update
    [PSU.kicad_sch, Sensors.kicad_sch]
2024-01-29 Started adding ICs to schematic
    [Control.kicad_sch, OpenHand.kicad_sch, Sensors.kicad_sch]
2024-01-30 Update schematic
    [Control.kicad_sch, OpenHand.kicad_sch, Sensors.kicad_sch]
2024-01-31 working on schematics
    [Control.kicad_sch, OpenHand.kicad_pcb, OpenHand.kicad_sch, PSU.kicad_sch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]
2024-02-08 Update ME, SCH and documentation a bit
    [Control.kicad_sch, OpenHand.f3d, PSU.kicad_sch, ProstheticHandTest.3mf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]
2024-02-08 Update mech design a bit
    Add some initial design prototype for checking out the idea/size/proportions
    [OpenHand.f3d, OpenHand.step]
2024-02-10 Minor updates to schm
    [Control.kicad_sch, OpenHand.kicad_pcb, OpenHand.kicad_sch, PSU.kicad_sch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]
2024-02-10 Update reference prototype model
    [OpenHand.f3d, OpenHand.step, finger.step]
2024-02-11 Update schematic a bit
    [Control.kicad_sch, PSU.kicad_sch, Sensors.kicad_sch]
2024-02-11 Update sch and board design
    [Control.kicad_sch, OpenHand.kicad_pcb, OpenHand.kicad_sch, PSU.kicad_sch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]
2024-02-13 Update schm
    [Control.kicad_sch, OpenHand.kicad_sch, PSU.kicad_sch, Sensors.kicad_sch]
2024-02-13 Update schm and pcb
    [Control.kicad_sch, OpenHand.kicad_pcb, OpenHand.kicad_sch, PSU.kicad_sch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]
2024-02-13 update schm and pcb again
    [Control.kicad_sch, ESP32.kicad_sch, OpenHand.kicad_pcb, OpenHand.kicad_sch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]
2024-02-15 Major updates to schm and pcb, a bit better design
    [MotorControl.kicad_sch, OpenHand.kicad_pcb, OpenHand.kicad_sch, PSU.kicad_sch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]
2024-02-16 done some routing
    [OpenHand.kicad_pcb]
2024-02-16 Finish first part of PCB layout and routing
    [OpenHand-B_Cu - Signal.gbr, OpenHand-B_Mask.gbr, OpenHand-B_Paste.gbr, OpenHand-B_Silkscreen.gbr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]
2024-03-16 Update PCB design/layout
    Still WIP, routing traces currently
    [OpenHand-B_Cu - Signal.gbr, OpenHand-B_Cu.gbr, OpenHand-B_Mask.gbr, OpenHand-B_Paste.gbr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]
2024-03-16 updated finger to add fasteners, ready for 2nd 3d printed prototype to determine finger positions.
    [ProstheticHand_V1_finger_rev0.61.STEP]
2024-03-26 Update PCB, add STLs from hand model
    [MotorControl.kicad_sch, OpenHand.kicad_pcb, OpenHand.kicad_sch, PSU.kicad_sch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]
2024-03-28 Update PCB and order it from JLCPCB
    [OpenHand-B_Cu.gbr, OpenHand-B_Mask.gbr, OpenHand-B_Silks.gbr, OpenHand-Edge_Cuts.gbr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]
2024-03-28 Update to KiCAD 8 and order components from LCSC
    [BOM.ods, MotorControl.kicad_sch, OpenHand.kicad_pcb, OpenHand.kicad_sch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]
2024-04-21 Update OpenHand PCB for V2 (WIP), update code (blinky)
    [BOM.ods, Control.kicad_sch, ESP32.kicad_sch, MotorControl.kicad_sch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]
2024-04-21 Update V2 schematic and start PCB layout
    [MotorControl.kicad_sch, OpenHand_v2.kicad_pcb, OpenHand_v2.kicad_sch, PSU.kicad_sch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]
2024-04-23 Add V2 PCB and update CubeIDE config for V2
    [MotorControl.kicad_sch, OpenHand_v2-B_Cu - Signal.gbr, OpenHand_v2-B_Mask.gbr, OpenHand_v2-B_Paste.gbr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]
2024-05-02 Finish OpenHand v2.0 board and prepare for ordering
    [OpenHand_v2-B_Cu - Signal.gbr, OpenHand_v2-B_Mask.gbr, OpenHand_v2-B_Paste.gbr, OpenHand_v2-B_Silkscreen.gbr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]
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2024-05-16 Update PCB and order from JLCPCB
    [OpenHand_v2-B_Cu - Signal.gbr, OpenHand_v2-B_Mask.gbr, OpenHand_v2-B_Paste.gbr, OpenHand_v2-B_Silkscreen.gbr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]
2024-06-16 EMG sensor quickfix, upadte ADC and DMA config
    [OpenHand_v2.kicad_pcb, OpenHand_v2.kicad_sch, PSU.kicad_sch, Sensors.kicad_sch]
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2024-06-30 Update mechanical hand and finger design
    [OpenHand Finger.f3d, OpenHand.f3d, OpenHand.step, OpenHand_v2.kicad_pcb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]
2024-10-09 Update SW part, prepare for simple presentation
    [Sensors.kicad_sch]
